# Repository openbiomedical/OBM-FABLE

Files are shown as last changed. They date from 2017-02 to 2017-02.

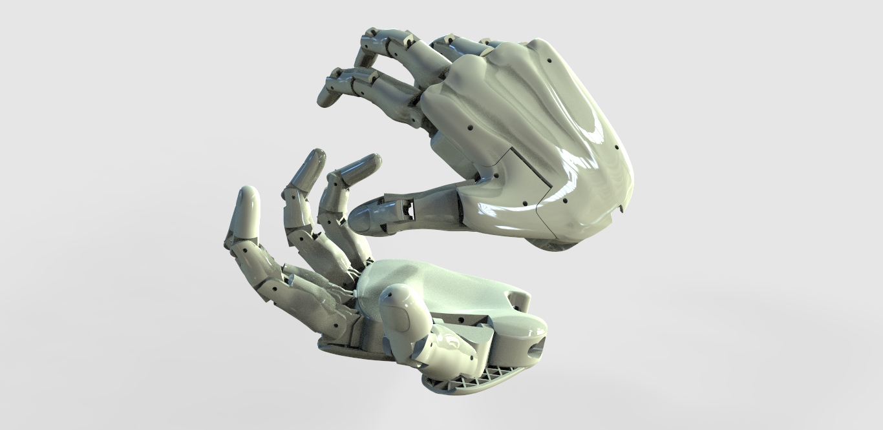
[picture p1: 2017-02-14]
3D Model/FABLE _V0.1 _April _2015/pics/2 posizione 2 bis.jpg

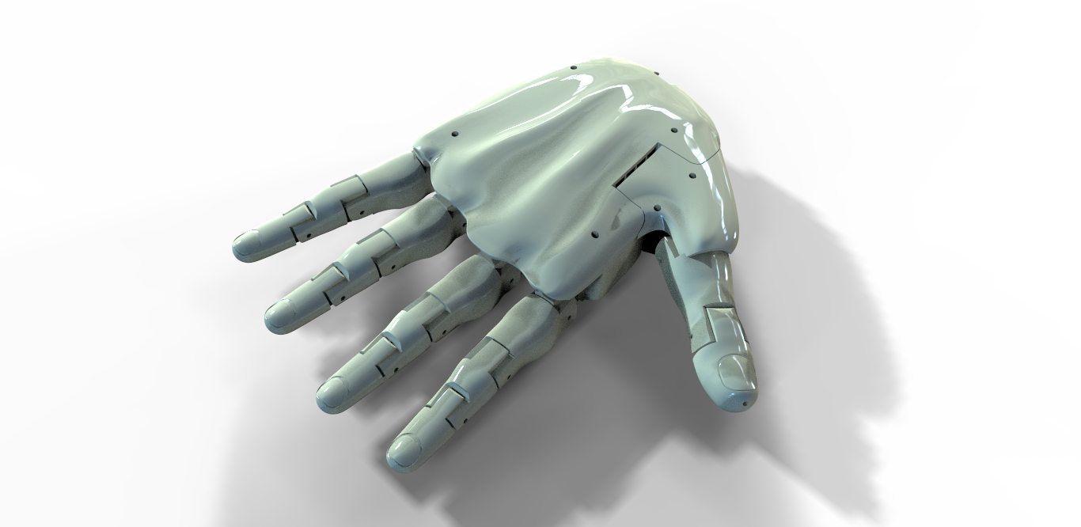
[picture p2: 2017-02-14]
3D Model/FABLE _V0.1 _April _2015/pics/1 luce 2.jpg

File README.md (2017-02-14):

# OBM-FABLE
FABLE is an electromechanical hand. Through the acquisition of signals generated by the muscles myoelectric contraction next to the elbow, it determines precise finger movements. Electronics is the hub of the system and it is compact, lowcost, completely reengineered to provide a project everywhere reproducible and technologically advanced. This hand is not a prosthesis, it is intended as a development kit. This work is licensed under the Creative Commons Attribution-NonCommercial-ShareAlike 4.0 International License. To view a copy of this license, visit https://creativecommons.org/licenses/by-nc-sa/4.0/legalcode

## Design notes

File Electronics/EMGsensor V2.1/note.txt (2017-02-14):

from Vin to electrodes only shield cable ( shield = pin2)

reference electrode = GND

supply from 5vdc to 12vdc (stab.)

R14 = gain

Shift = output with offset (Vcc/2)

no_shift = Output without offset (Vcc/2)

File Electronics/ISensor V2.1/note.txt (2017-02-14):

Resistor smd 2512 package

PS1,..,PS6 = to arduino [ PWM = pin3 ; Analog Input = pin1 ]

S1,...,S6 = From servo  [ PWM = Pin3 ; VCC = Pin2 ; GND = pin1 to resistor ]

VCC = 6v dc Max from step-down

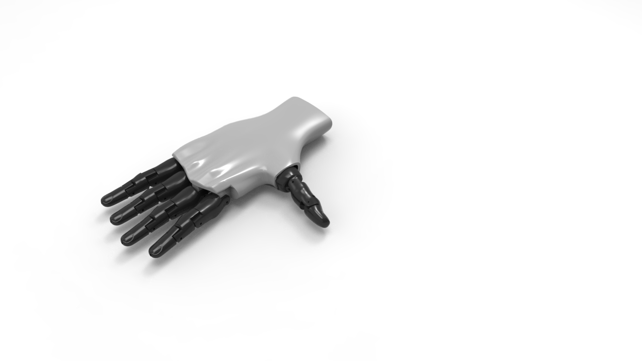
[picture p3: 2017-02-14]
3D Model/FABLE V0.2 August 2015/pics/untitled.222.jpg

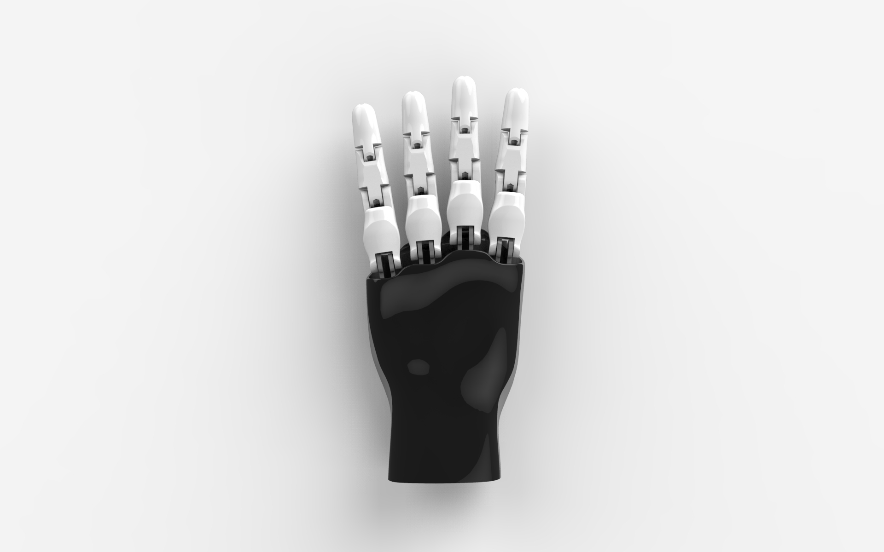
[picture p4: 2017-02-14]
3D Model/FABLE V0.2 August 2015/pics/untitled.328.jpg

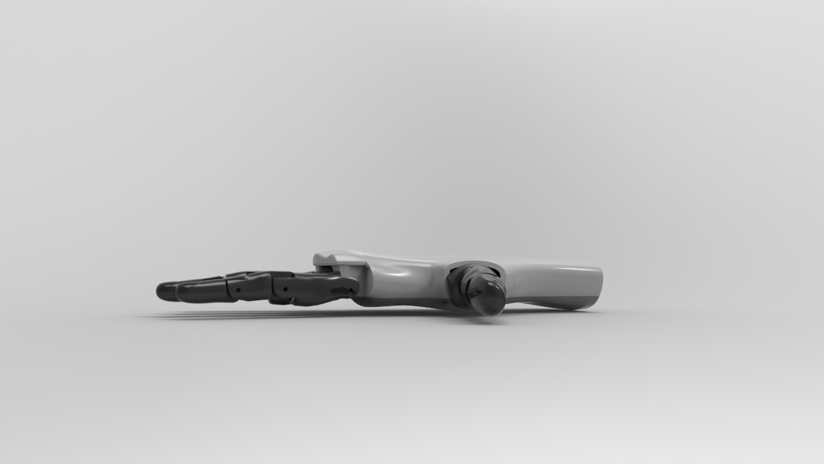
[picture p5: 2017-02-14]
3D Model/FABLE V0.2 August 2015/pics/untitled.223.jpg

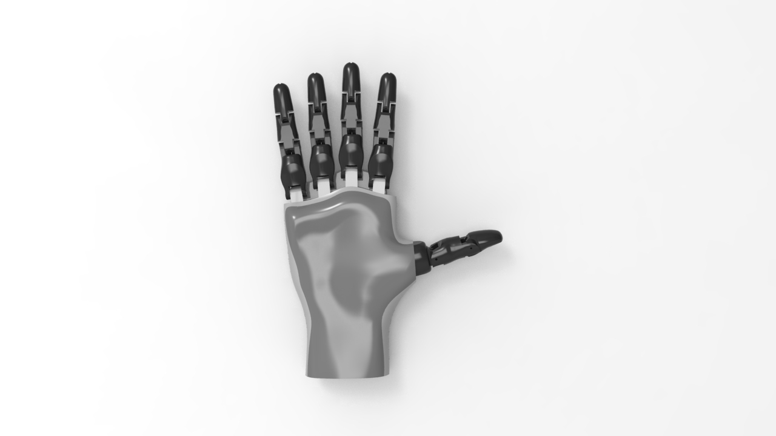
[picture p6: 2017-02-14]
3D Model/FABLE V0.2 August 2015/pics/untitled.217.jpg

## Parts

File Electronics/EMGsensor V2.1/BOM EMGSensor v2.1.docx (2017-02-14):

Componenti EMGSensor v2.1

Resistors | Pz. | Codice | Link
3,9k 1% | 2 | | http://www.mouser.it/ProductDetail/KOA-Speer/MF1-4DCT52R3901F/?qs=sGAEpiMZZMsPqMdJzcrNwk4M%252bI85OEMF%252b8B6SFnC314%3d
2,7k 1% | 1 | | http://www.mouser.it/ProductDetail/KOA-Speer/MF1-4DCT52R2701F/?qs=sGAEpiMZZMsPqMdJzcrNwk4M%252bI85OEMFHm1ljwxmljk%3d
330k 1% | 4 | | http://www.mouser.it/ProductDetail/KOA-Speer/MF1-4DCT52R3303F/?qs=sGAEpiMZZMsPqMdJzcrNwk4M%252bI85OEMF4k6263vO8XI%3d
150k 1% | 2 | | http://www.mouser.it/ProductDetail/KOA-Speer/MF1-4CCT52R1503F/?qs=sGAEpiMZZMsPqMdJzcrNwk4M%252bI85OEMFH8UroyRjCLw%3d
10k 1% | 3 | | http://www.mouser.it/ProductDetail/KOA-Speer/MF1-4DCT52A1002F/?qs=sGAEpiMZZMsPqMdJzcrNwuecx6lsmnwYT8hyjLelWtY%3d
22k 1% | 3 | | http://www.mouser.it/ProductDetail/KOA-Speer/MF1-4CCT52R2202F/?qs=sGAEpiMZZMsPqMdJzcrNwk4M%252bI85OEMFeFz33mmpMTA%3d
100k trim | 1 | | http://www.mouser.it/ProductDetail/BI-Technologies-TT-Electronics/25PR100KLF/?qs=sGAEpiMZZMvygUB3GLcD7jZSyzxDqivkrwCWYpHkBsI%3d

Capacitors | Pz | Codice | Link
1nF 5% | 2 | | http://www.mouser.it/ProductDetail/Kemet/R82EC1100DQ50J/?qs=sGAEpiMZZMv1cc3ydrPrF512ADDNLQZJj36DMWUqyRU%3d
10nF 5% | 1 | | http://www.mouser.it/ProductDetail/WIMA/FKP2-01-63-5/?qs=sGAEpiMZZMv1cc3ydrPrF9SBthQCDPcr2mIDPeCmXKk%3d
47 uF 16v | 1 | | http://www.mouser.it/ProductDetail/Kemet/ESH476M016AC3AA/?qs=sGAEpiMZZMvwFf0viD3Y3Z8dpVAM7bD5NxuBo6CNc2U%3d
100nF | 3 | | http://www.mouser.it/ProductDetail/Xicon/140-50U5-104M-RC/?qs=sGAEpiMZZMt1mVBmZSXTPPQUnq7ol7tGZljKIuTg6iI%3d
33nF | 4 | | http://www.mouser.it/ProductDetail/WIMA/MKS20-033-63-10/?qs=sGAEpiMZZMv1cc3ydrPrF9fbJRxYhp3ITJ3n2D%252bCNEc%3d
3,9nF | 2 | | http://www.mouser.it/ProductDetail/Kemet/MMK5392J63J01L165TR18/?qs=sGAEpiMZZMv1cc3ydrPrF17gIuUB4mH1M9xivW0kULQ%3d

Ic, diode | Pz. | Codice | Link
schotty | 1 | | http://www.mouser.it/ProductDetail/STMicroelectronics/STPS2150/?qs=sGAEpiMZZMtQ8nqTKtFS%2fM2amOy8Xbj2uDkMBx8%252beH4%3d
Ad623br | 1 | | http://www.mouser.it/ProductDetail/Analog-Devices/AD623BNZ/?qs=sGAEpiMZZMv9Q1JI0Mo%2fteUpiLyE8W1%2f
Opa4342 | 1 | | http://www.mouser.it/ProductDetail/Texas-Instruments/OPA4342PA/?qs=sGAEpiMZZMtCHixnSjNA6Mrdwin7F8A2Bb6eRblE8YI%3d

vari | Pz. | Codice | Link
Socket 8pin | 1 | | http://it.rs-online.com/web/p/zoccoli-dil/6742479/
Socket 14pin | 1 | | http://it.rs-online.com/web/p/zoccoli-dil/6742476/
Porta batterie | 1 | | http://www.mouser.it/ProductDetail/Keystone-Electronics/1049P/?qs=sGAEpiMZZMt13fpse6CWDXAPAJ%2f5HJNvHuGSwYCxUME7UjRmTs2TpQ%3d%3d

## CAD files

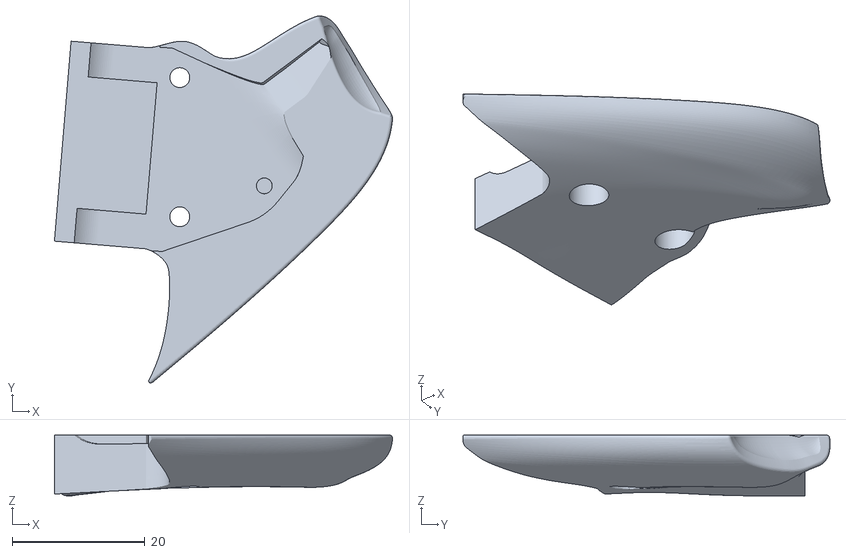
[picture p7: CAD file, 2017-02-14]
3D Model/FABLE _V0.1 _April _2015/stl_v0.1/Copertura snodo/copertura snodo008.stl
51.0 x 55.4 x 9.19

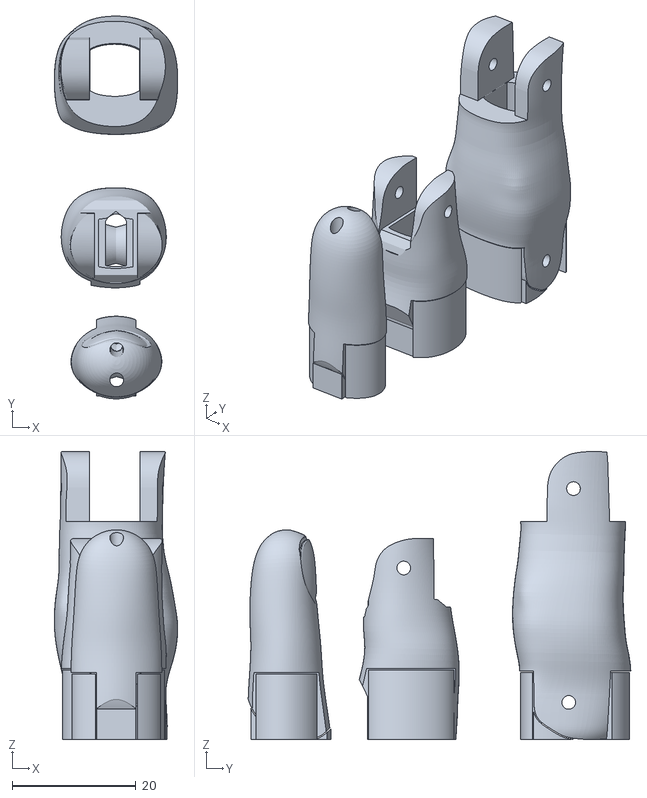
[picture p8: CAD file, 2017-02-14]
3D Model/FABLE _V0.1 _April _2015/stl_v0.1/Dita/dita 002 Supporti.stl
20.0 x 61.9 x 46.6

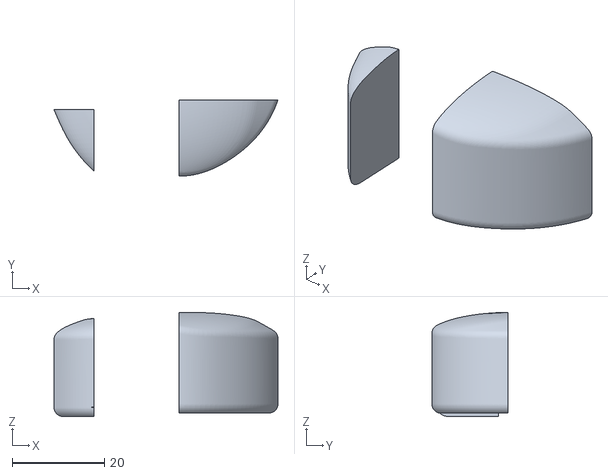
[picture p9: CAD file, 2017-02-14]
3D Model/FABLE _V0.1 _April _2015/stl_v0.1/Pezzi Palmo/pezzi_palmo001.stl
48.5 x 16.5 x 22.6

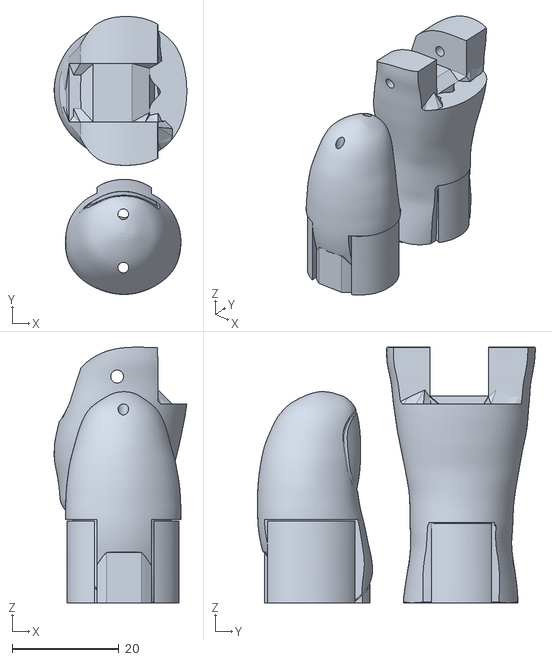
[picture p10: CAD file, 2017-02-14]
3D Model/FABLE _V0.1 _April _2015/stl_v0.1/Pollice/pollice001 supporti.stl
24.9 x 52.2 x 48.0

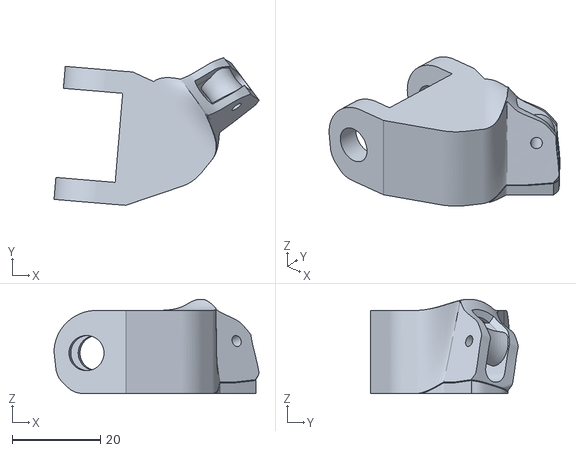
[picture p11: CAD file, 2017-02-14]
3D Model/FABLE _V0.1 _April _2015/stl_v0.1/Snodo/snodo004 supporto.stl
46.5 x 33.5 x 21.4

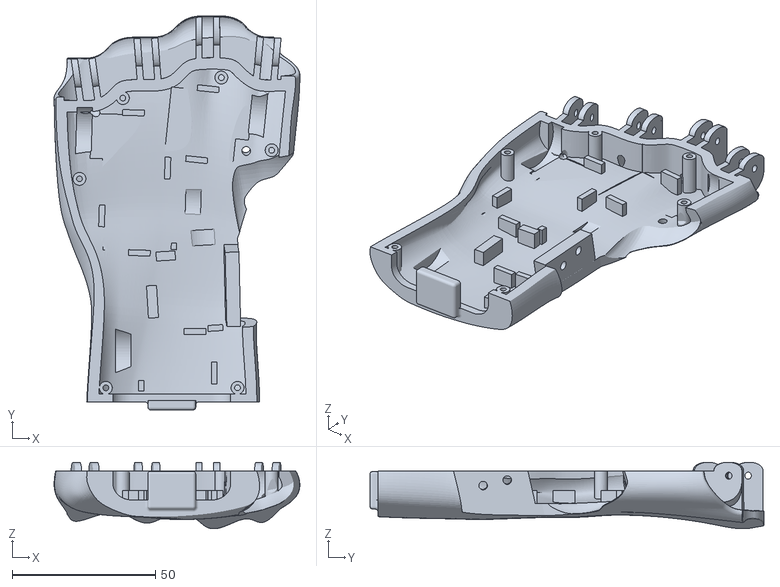
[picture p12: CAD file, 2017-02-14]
3D Model/FABLE V0.2 August 2015/STL v0.2 agosto 2015/dorso.stl
85.7 x 137.4 x 23.2

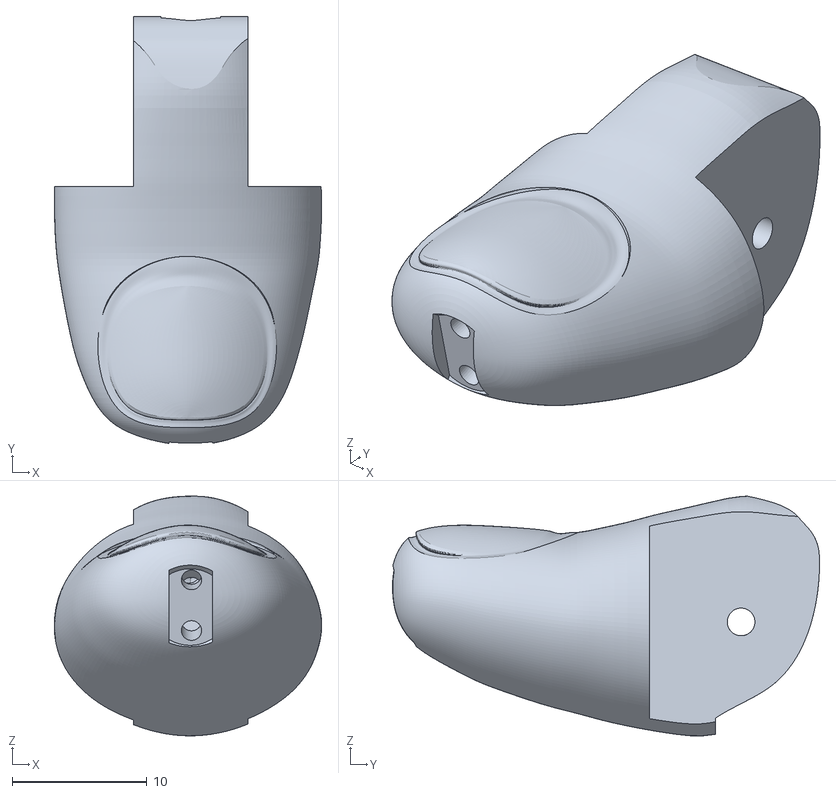
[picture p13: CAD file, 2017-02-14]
3D Model/FABLE V0.2 August 2015/STL v0.2 agosto 2015/stl_dita/pollice2.stl
19.9 x 31.7 x 17.8

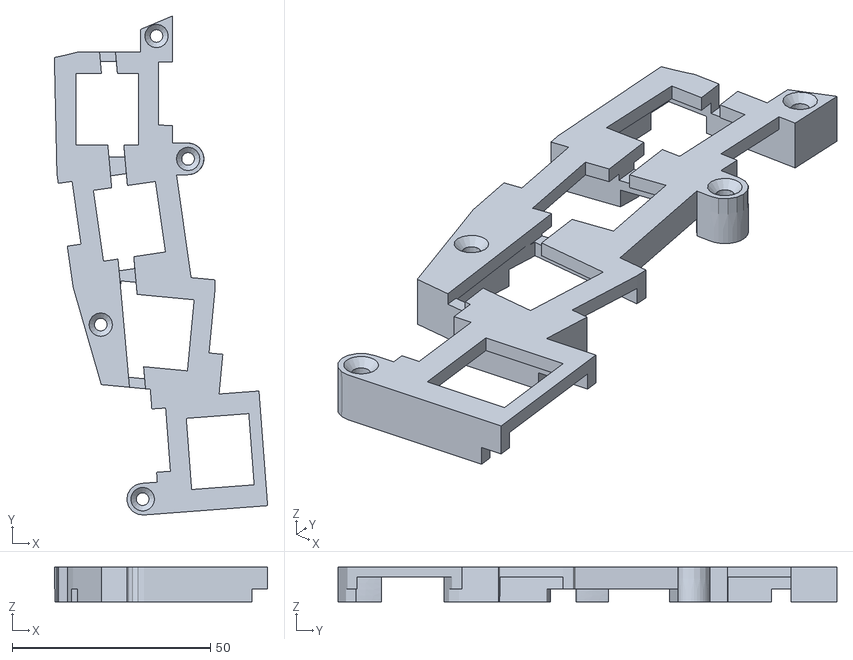
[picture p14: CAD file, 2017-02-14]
3D Model/fable v0.3 January 2016/FABLE V0.3 STL january 2016/coperchio servo.stl
53.8 x 125.8 x 8.80

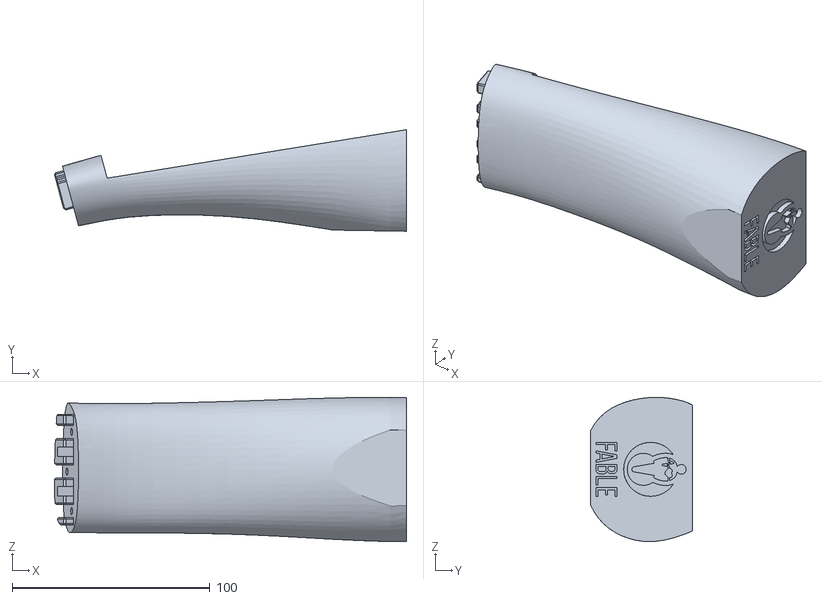
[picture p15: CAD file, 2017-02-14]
3D Model/FABLE V0.4 September 2016/STL V0.4/support front arm stl/support front.stl
178.0 x 51.4 x 72.9

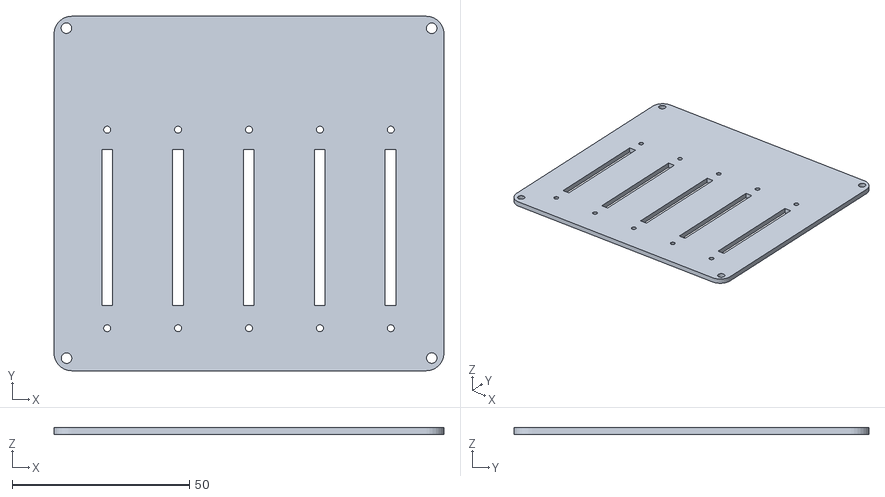
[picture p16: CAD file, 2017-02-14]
3D Model/FABLE V0.4 September 2016/STL V0.4/support pot stl/plate pot.stl
110.0 x 100.0 x 2.00

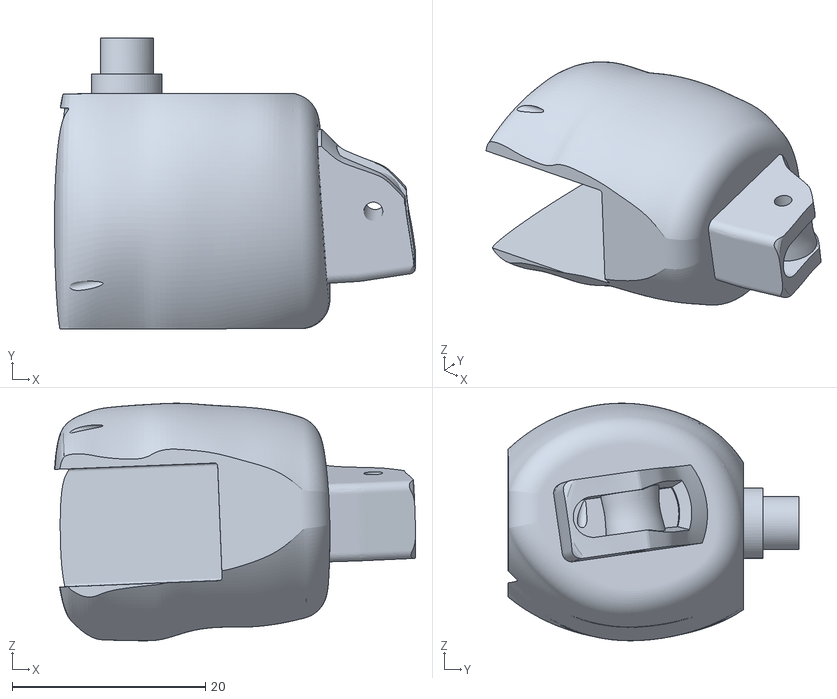
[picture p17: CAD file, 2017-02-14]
3D Model/FABLE V0.2 August 2015/STL v0.2 agosto 2015/snodo pollice.stl
37.4 x 30.2 x 24.6

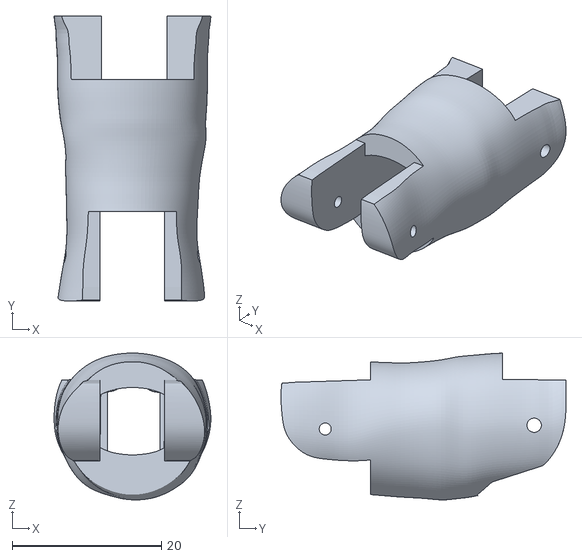
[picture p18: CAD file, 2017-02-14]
3D Model/FABLE V0.2 August 2015/STL v0.2 agosto 2015/stl_dita/pollice1.stl
21.0 x 38.2 x 19.7

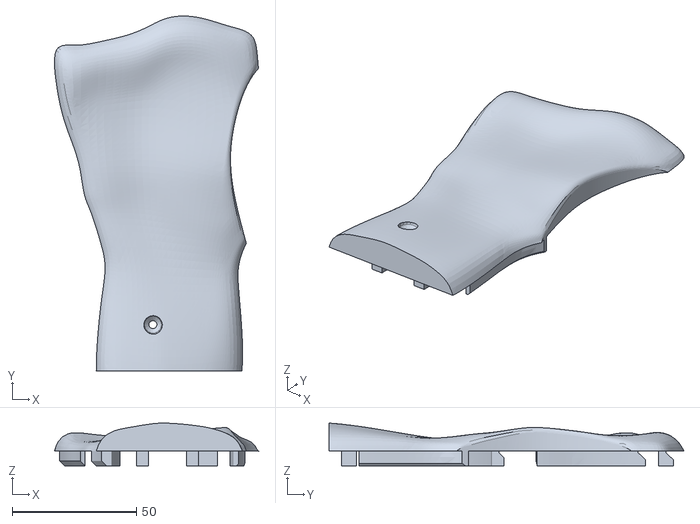
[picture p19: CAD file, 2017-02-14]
3D Model/fable v0.3 January 2016/FABLE V0.3 STL january 2016/palmo fable.stl
82.1 x 142.9 x 17.3

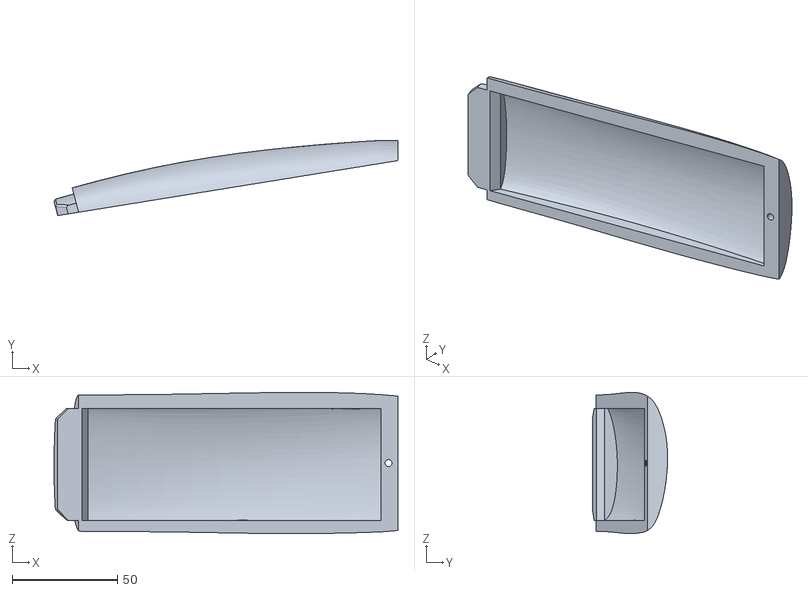
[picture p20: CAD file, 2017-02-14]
3D Model/FABLE V0.4 September 2016/STL V0.4/support front arm stl/support back.stl
163.1 x 35.7 x 66.9

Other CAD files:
3D Model/FABLE V0.4 September 2016/STL V0.4/support pot stl/structure.stl
3D Model/FABLE V0.2 August 2015/STL v0.2 agosto 2015/palmo.stl
3D Model/FABLE V0.2 August 2015/STL v0.2 agosto 2015/stl_dita/dito3.stl
3D Model/FABLE V0.4 September 2016/STL V0.4/support pot stl/plate arduino nano.stl
3D Model/FABLE V0.2 August 2015/STL v0.2 agosto 2015/blocco1.stl
3D Model/FABLE V0.2 August 2015/STL v0.2 agosto 2015/blocco2.stl
3D Model/FABLE V0.2 August 2015/STL v0.2 agosto 2015/stl_dita/dito1.stl
3D Model/FABLE V0.2 August 2015/STL v0.2 agosto 2015/stl_dita/dito2.stl
3D Model/FABLE V0.2 August 2015/STL v0.2 agosto 2015/stl_dita/falange orizzontale supporto.stl
3D Model/FABLE V0.4 September 2016/3dm v0.4/hand/finger.3dm
3D Model/FABLE V0.4 September 2016/3dm v0.4/hand/hand back.3dm
3D Model/FABLE V0.4 September 2016/3dm v0.4/hand/hand palm.3dm
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

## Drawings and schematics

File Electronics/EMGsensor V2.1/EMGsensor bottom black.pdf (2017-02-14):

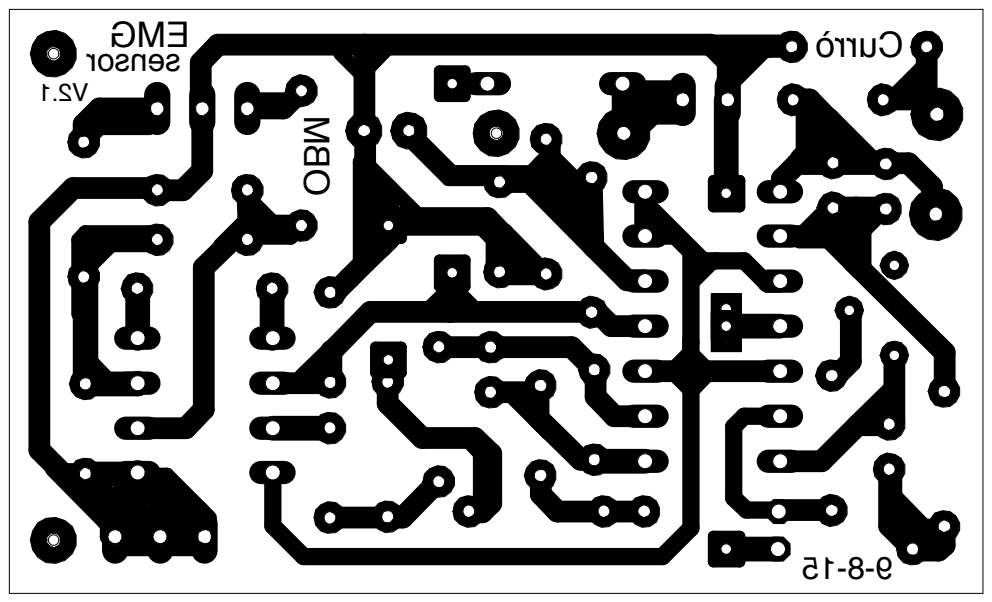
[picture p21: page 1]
EMG sensorV2.1; OBM; Currò

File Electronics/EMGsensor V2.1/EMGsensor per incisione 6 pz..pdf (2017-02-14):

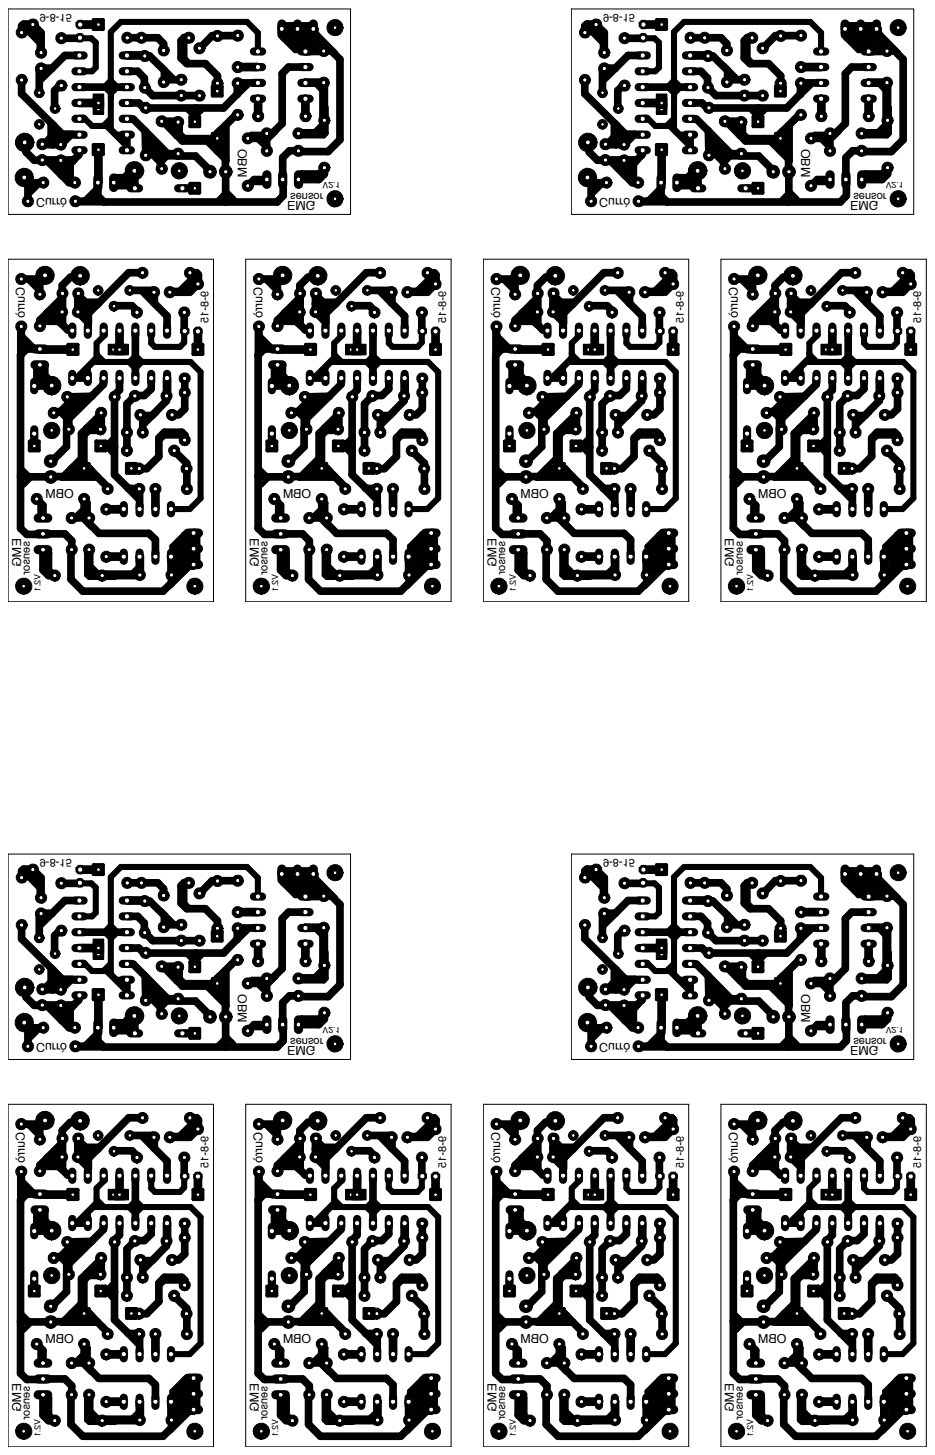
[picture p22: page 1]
EMG sensor; Currò; EMG; sensorV2.1; OBM

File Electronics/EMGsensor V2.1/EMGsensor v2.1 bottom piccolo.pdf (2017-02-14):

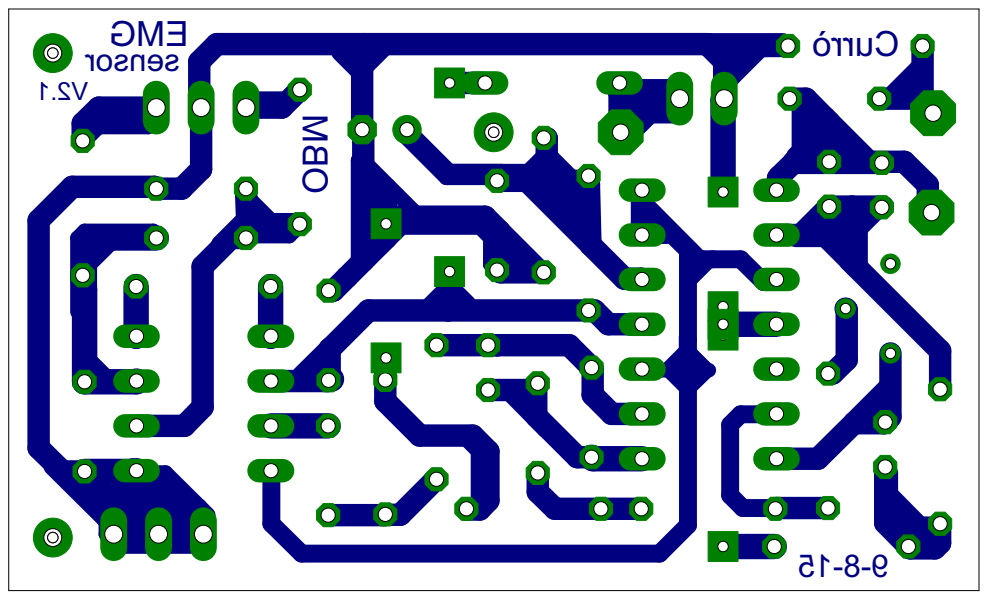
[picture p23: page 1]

GME r osnes 1. 2V OBM òrr uC 51- 8- 9

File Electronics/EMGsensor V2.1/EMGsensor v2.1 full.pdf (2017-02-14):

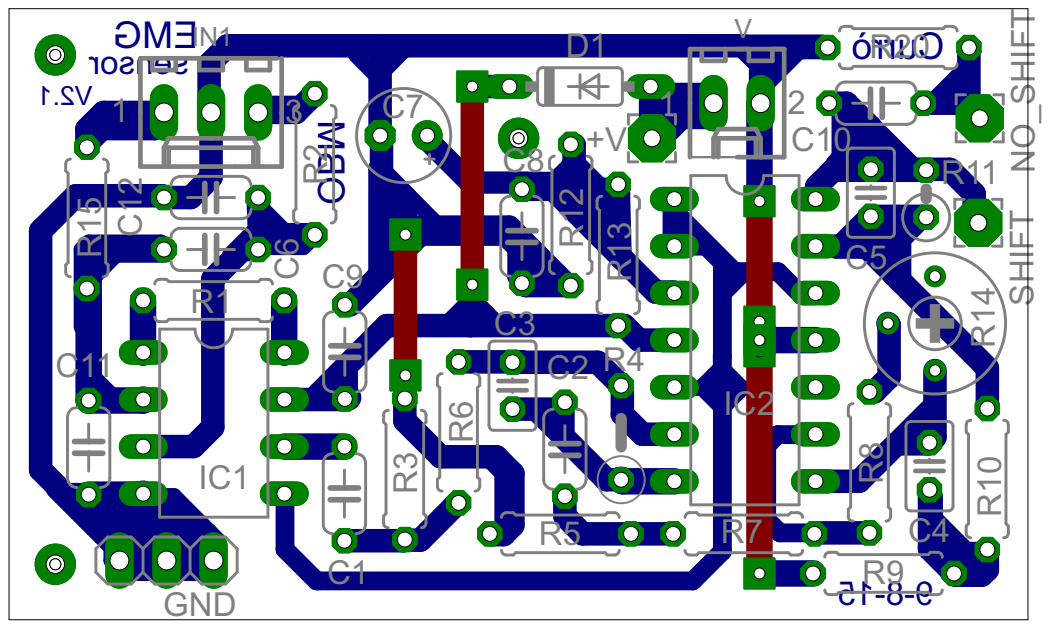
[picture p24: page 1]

GME r osnes 1. 2V OBM òrr uC 51- 8- 9 1 1 2 3 C1 C2 C3 C4 C5 C7 C8 C9 D1 IC1 IC2 NO_SHIFT SHIFT R1 R10 R12 R13 R14 R3 R4 R5 R6 R7 R8 R9 +V V GND R20 C10 C6 C11 C12R2 R15 IN1 R11

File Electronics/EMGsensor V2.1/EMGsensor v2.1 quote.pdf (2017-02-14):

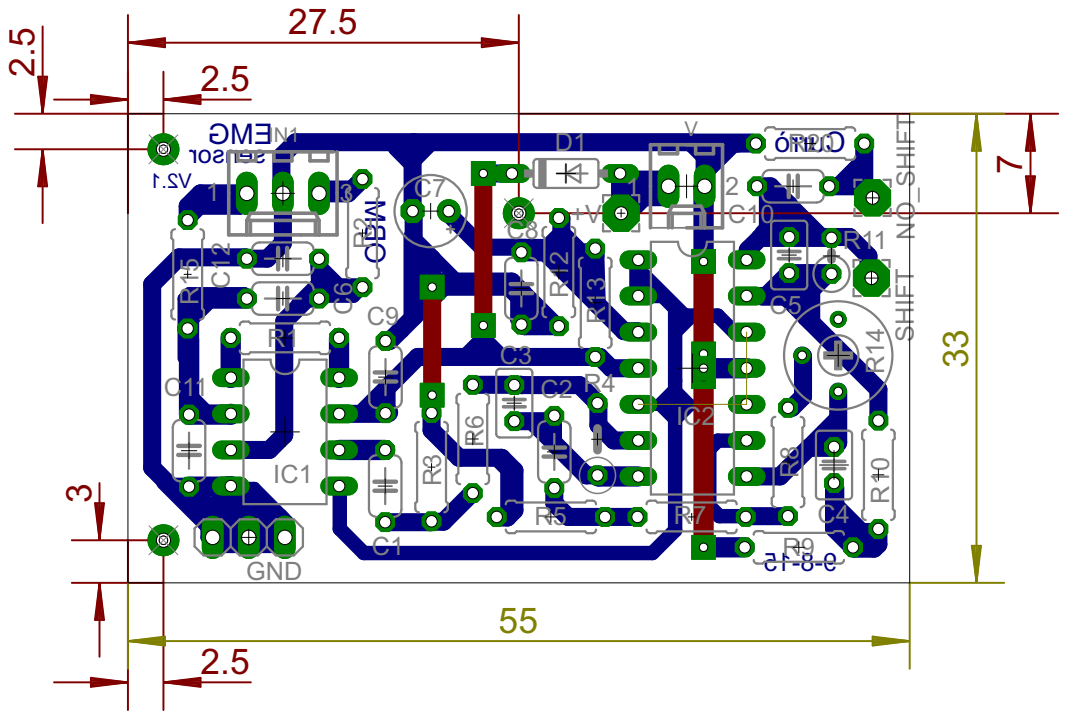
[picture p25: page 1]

GME r osnes 1. 2V OBM òrr uC 51- 8- 9 2.5 2.5 2.5 3 27.5 7 1 1 2 3 C1 C2 C3 C4 C5 C7 C8 C9 D1 IC1 IC2 NO_SHIFT SHIFT R1 R10 R12 R13 R14 R3 R4 R5 R6 R7 R8 R9 +V V GND R20 C10 C6 C11 C12R2 R15 IN1 R11 55 33

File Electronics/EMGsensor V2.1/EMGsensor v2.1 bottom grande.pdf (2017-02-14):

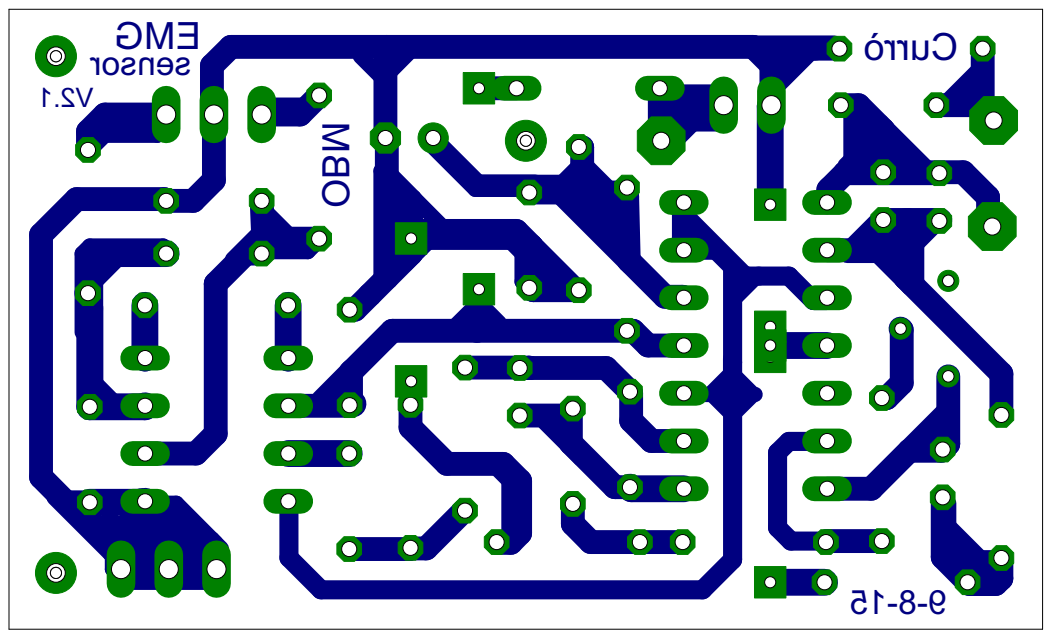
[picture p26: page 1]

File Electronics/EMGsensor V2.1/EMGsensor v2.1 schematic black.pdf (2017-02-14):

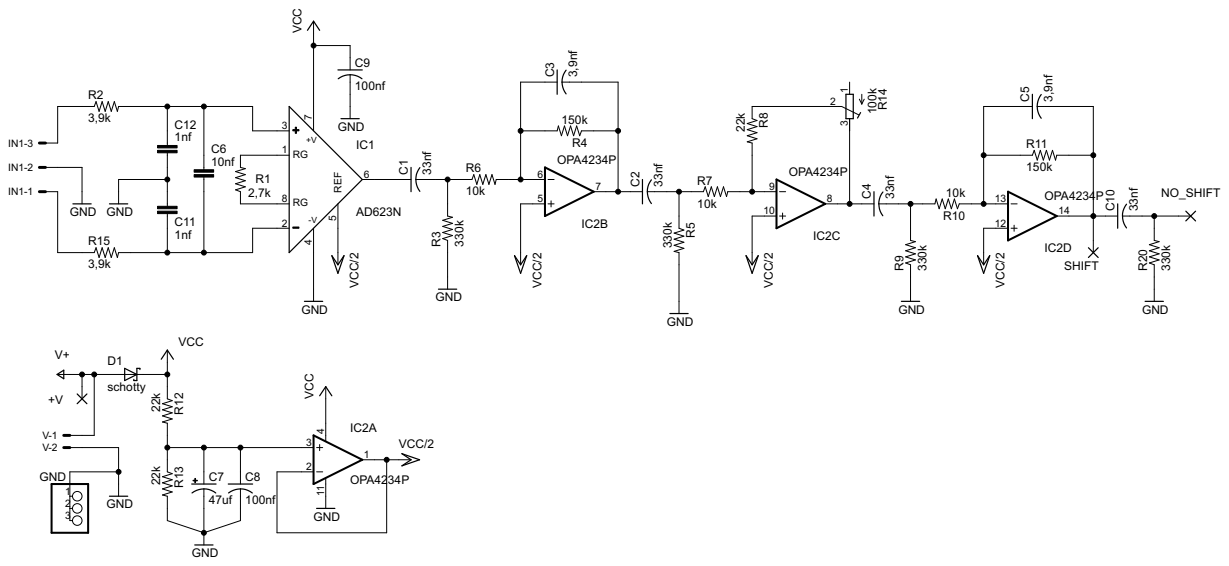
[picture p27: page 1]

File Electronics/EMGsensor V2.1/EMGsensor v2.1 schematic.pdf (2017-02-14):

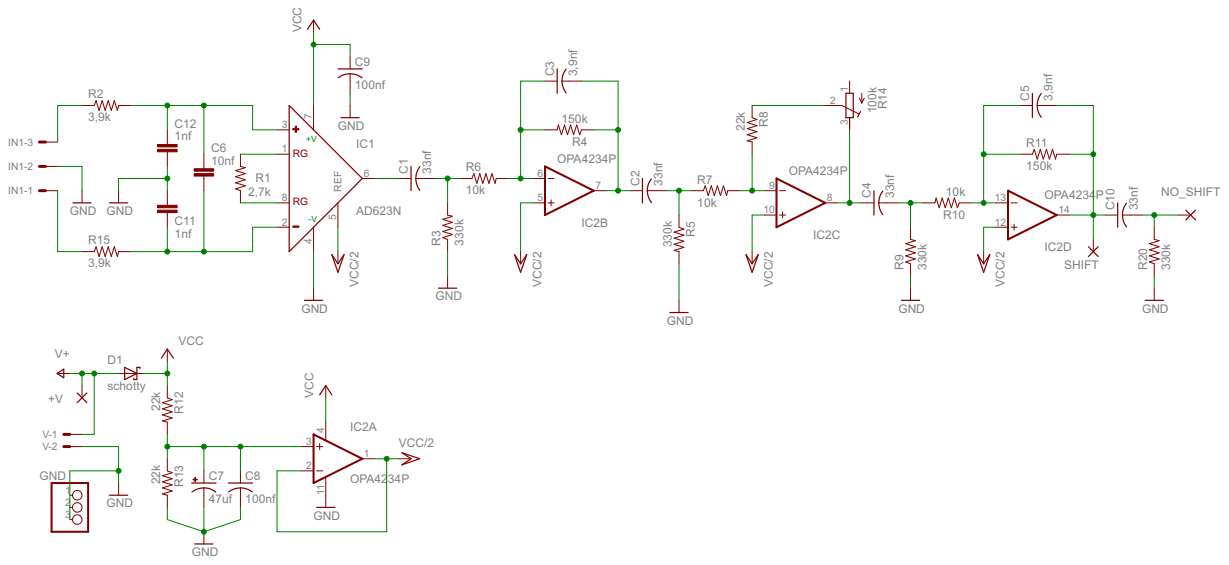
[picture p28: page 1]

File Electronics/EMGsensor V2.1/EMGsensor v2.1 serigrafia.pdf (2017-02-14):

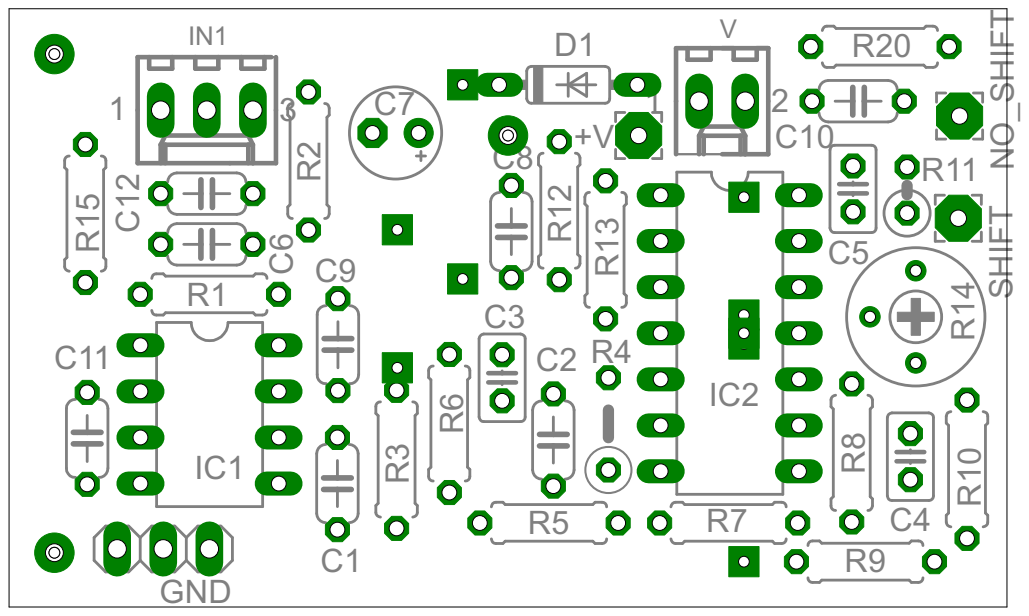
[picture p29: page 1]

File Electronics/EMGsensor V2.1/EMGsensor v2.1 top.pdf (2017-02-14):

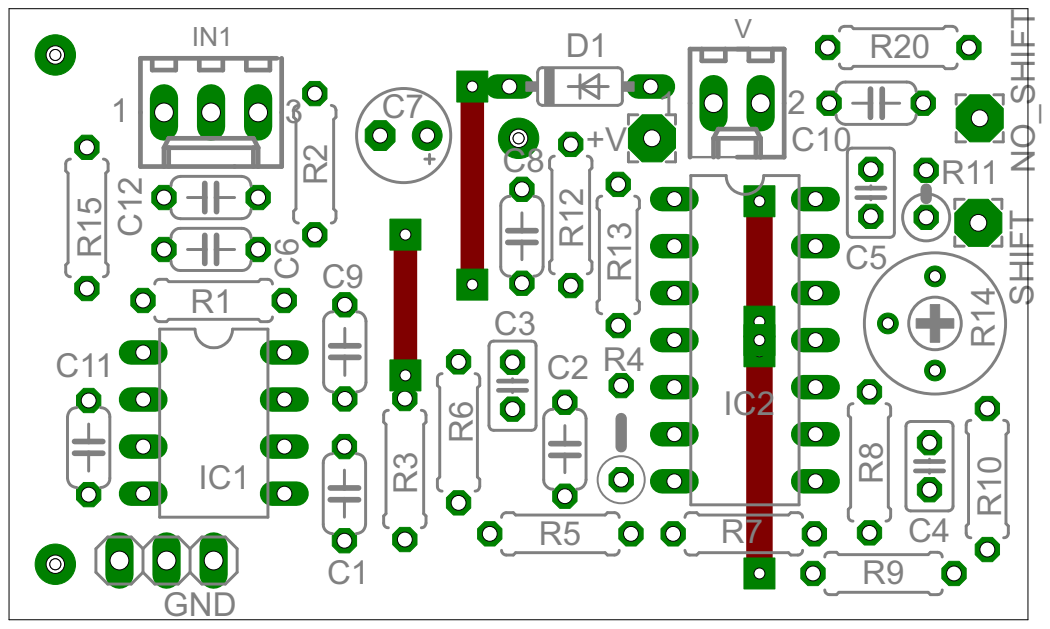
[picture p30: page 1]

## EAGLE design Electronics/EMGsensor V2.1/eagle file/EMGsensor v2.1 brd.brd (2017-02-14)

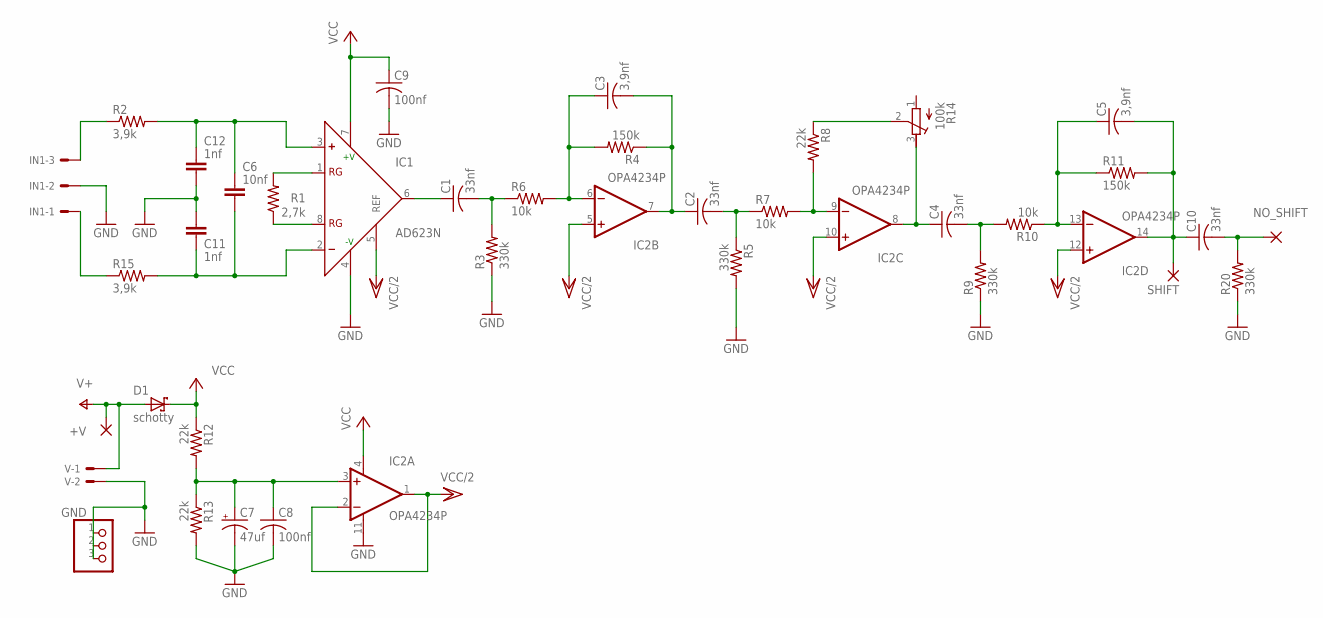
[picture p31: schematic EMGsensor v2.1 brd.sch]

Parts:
+V: 2,54/0,9
C1, C2, C10: 33nf; C050-024X044
C3, C5: 3,9nf; C025-025X050
C4: 33nf; C025-025X050
C6: 10nf; C050-024X044
C7: 47uf; E2,5-5
C8, C9: 100nf; C050-024X044
C11, C12: 1nf; C050-024X044
D1: schotty; DO35-7
GND: PINHD-1X3; 1X03
IC1: AD623N; DIL08
IC2: OPA4234P; DIL14
IN1: 22-27-2031-03; 6410-03
NO_SHIFT: 2,54/0,9
R1: 2,7k; 0207/7
R2, R15: 3,9k; 0207/7
R3, R5, R9, R20: 330k; 0207/7
R4: 150k; 0207/5V
R6, R7, R10: 10k; 0207/7
R8, R12, R13: 22k; 0207/7
R11: 150k; 0207/2V
R14: 100k; RTRIM3339P
SHIFT: 2,54/0,9
V: 22-27-2021-02; 6410-02

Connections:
unnamed: C1.1, IC1.6 (OUT)
unnamed: C1.2, R3.2, R6.1
unnamed: C3.1, IC2.6 (-IN), R4.2, R6.2
unnamed: C2.1, C3.2, IC2.7 (OUT), R4.1
unnamed: C2.2, R5.1, R7.1
unnamed: IC2.9 (-IN), R7.2, R8.2
unnamed: C4.1, IC2.8 (OUT), R14.3 (E)
unnamed: C4.2, R9.2, R10.2
unnamed: C5.1, IC2.13 (-IN), R10.1, R11.1
unnamed: C5.2, C10.1, IC2.14 (OUT), R11.2, SHIFT.1
unnamed: R8.1, R14.2 (S)
unnamed: IC1.1 (RG), R1.2
unnamed: C6.1, C12.1, IC1.3 (+), R2.2
unnamed: C6.2, C11.2, IC1.2 (-), R15.2
unnamed: IN1.3, R2.1
unnamed: C10.2, NO_SHIFT.1, R20.2
unnamed: IN1.1, R15.1
unnamed: IC1.5 (REF), IC2.1 (OUT), IC2.2 (-IN)
unnamed: C9.1, D1.C, IC1.7 (+V), IC2.4 (V+), R12.1
unnamed: C7.+, C8.1, IC2.3 (+IN), R12.2, R13.1
unnamed: +V.1, D1.A, V.1
unnamed: IC1.8 (RG), R1.1
unnamed: C7.-, C8.2, C9.2, C11.1, C12.2, GND.1, GND.2, GND.3, IC1.4 (-V), IC2.11 (V-), IN1.2, R3.1, R5.2, R9.1, R13.2, R20.1, V.2
VCC/2: IC2.5 (+IN), IC2.10 (+IN), IC2.12 (+IN)

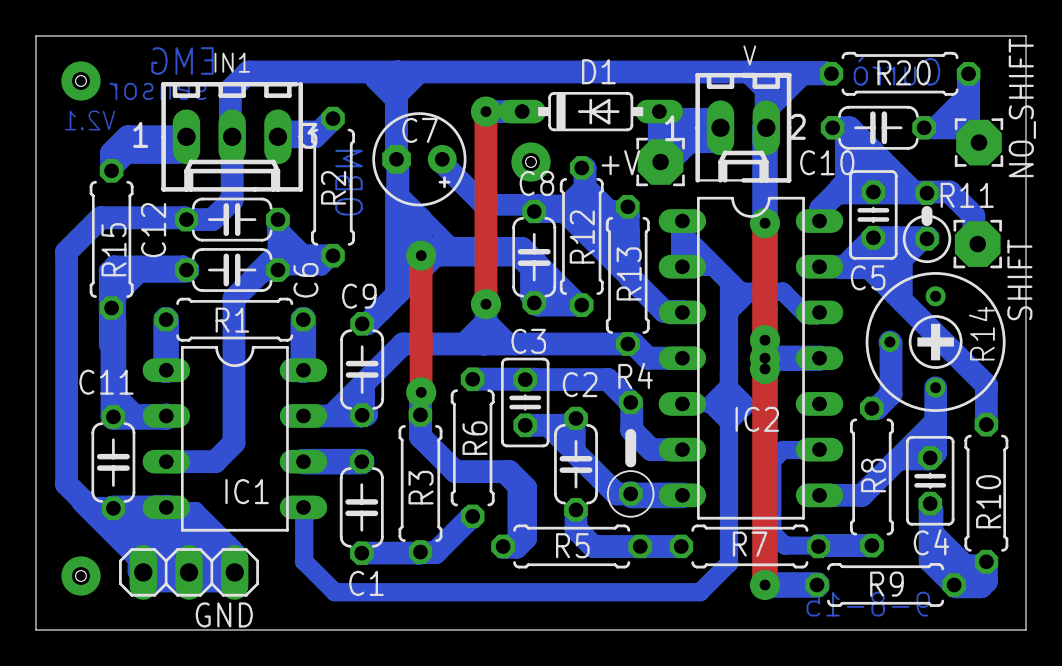
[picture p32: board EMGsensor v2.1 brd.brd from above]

Board: 2 copper layers, 55.0 x 33.0 mm, 37 parts (0 on the bottom side), 24 nets.

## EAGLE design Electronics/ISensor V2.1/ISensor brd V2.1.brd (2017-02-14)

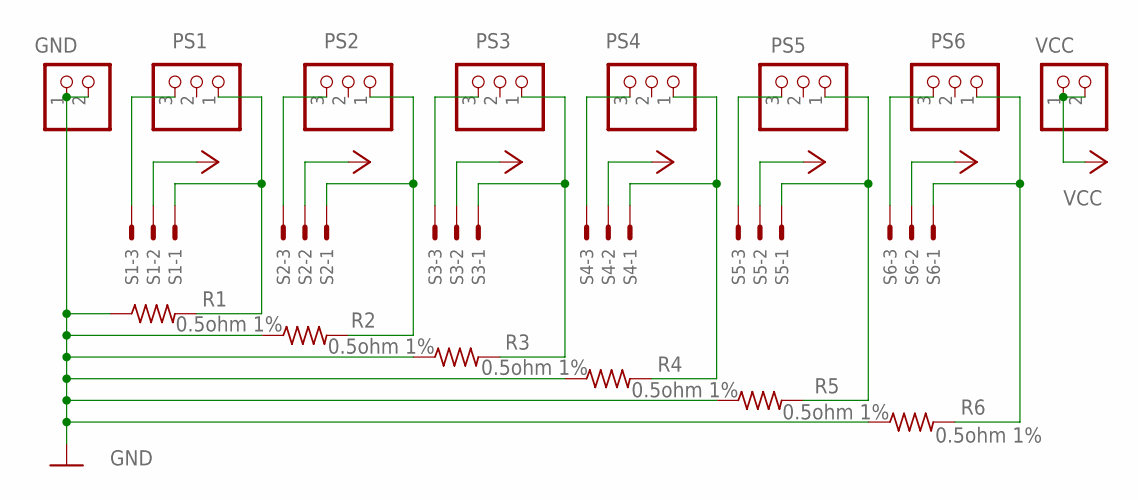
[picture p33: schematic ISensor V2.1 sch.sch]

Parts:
GND: PINHD-1X2; 1X02
PS1, PS2, PS3, PS4, PS5, PS6: PINHD-1X3; 1X03
R1, R2, R3, R4, R5, R6: 0.5ohm 1%; R2512
S1, S2, S3, S4, S5, S6: 22-27-2031-03; 6410-03
VCC: PINHD-1X2; 1X02

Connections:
unnamed: PS1.3, S1.3
unnamed: PS1.1, R1.2, S1.1
unnamed: PS2.1, R2.2, S2.1
unnamed: PS3.3, S3.3
unnamed: PS3.1, R3.2, S3.1
unnamed: PS4.3, S4.3
unnamed: PS4.1, R4.2, S4.1
unnamed: PS5.3, S5.3
unnamed: PS5.1, R5.2, S5.1
unnamed: PS6.3, S6.3
unnamed: PS6.1, R6.2, S6.1
unnamed: GND.1, GND.2, R1.1, R2.1, R3.1, R4.1, R5.1, R6.1
PS2: PS2.3, S2.3
VCC: S1.2, S2.2, S3.2, S4.2, S5.2, S6.2, VCC.1, VCC.2

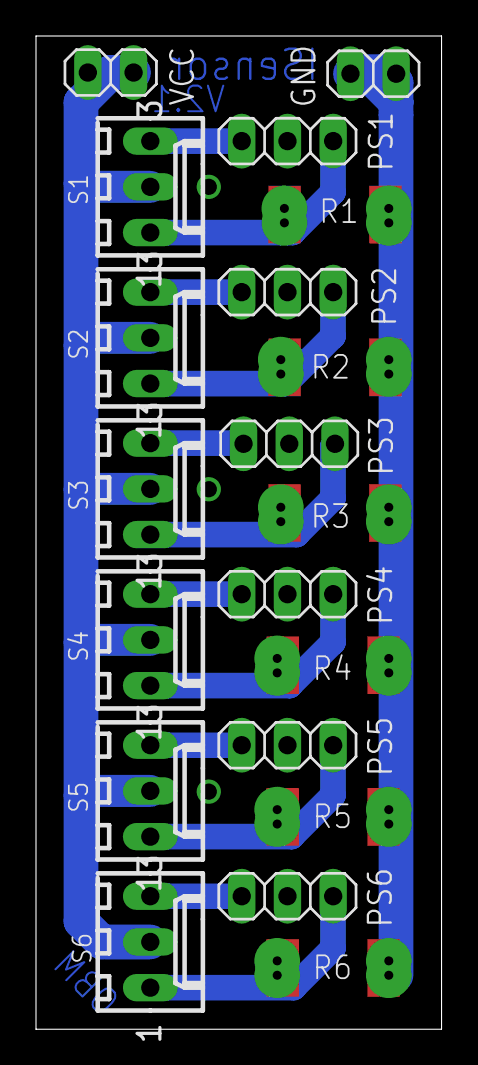
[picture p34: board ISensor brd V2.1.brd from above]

Board: 2 copper layers, 22.5 x 55.2 mm, 20 parts (0 on the bottom side), 14 nets.

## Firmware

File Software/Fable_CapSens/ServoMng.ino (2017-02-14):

int GetServoPos(int ServoIndex){
  return ArmoMov.angolo[ServoIndex];
  }
void SetServoPos(int ServoIndex, int Pos){
  ArmoMov.Pos[ServoIndex]=Pos;  
  }
  
void SetServoAngleMin (int ServoIndex,int AngleMin){
  FABLE_InfoParameter.OpenAngleTarget[ServoIndex]=AngleMin;
  }

void SetServoAngleMax (int ServoIndex,int AngleMax){
  FABLE_InfoParameter.CloseAngleTarget[ServoIndex]=AngleMax;
  }
void SetEnableFinger(int FingerCode){
  }
int GetEnablefinger(){
   int EnableCount=0;
   for (int i =0;i<NumServo;i++)
    EnableCount+=FABLE_InfoParameter.FingerEnabled[i];
  return EnableCount;
  }  
int GetServoAngleMin (int ServoIndex){
  return FABLE_InfoParameter.OpenAngleTarget[ServoIndex];
  }

 int GetServoAngleMax (int ServoIndex){
  return FABLE_InfoParameter.CloseAngleTarget[ServoIndex];
  }

int GetServoSpeed(){
  return FABLE_InfoParameter.Speed;
   }

void SetServoSpeed(int Speed){
  FABLE_InfoParameter.Speed=Speed;
  }



void MoveServo(int ServoIndex){
  
  int Speed=GetServoSpeed();
  int anglemin=GetServoAngleMin(ServoIndex);
  int anglemax=GetServoAngleMax(ServoIndex);
  float Stepmin=(anglemax-anglemin);
  float AngleStep=(Stepmin*Speed)/1048 ;
  int CurrPos=GetServoPos(ServoIndex);
  
 // Serial.println(Stepmin);
 // Serial.println(anglemin);
 // Serial.println(anglemax);
 // Serial.println(AngleStep);
  if (ArmoMov.Pos[ServoIndex]<CurrPos){
      AngleStep=-AngleStep;
      while(ArmoMov.grado[ServoIndex]>ArmoMov.Pos[ServoIndex])
      {ServoMovement(ServoIndex,AngleStep);
      Serial.println(ArmoMov.grado[ServoIndex]);}
      
      }
   else{
    while(ArmoMov.grado[ServoIndex]<ArmoMov.Pos[ServoIndex])
    {ServoMovement(ServoIndex,AngleStep);
    Serial.println(ArmoMov.grado[ServoIndex]);}
    
    }
  
  
  }
  
void MoveFinger(int index,int Pos){
  SetServoPos(index,Pos);
  MoveServo(index);
  
  }

void OpenHand(){
  for (int i=0;i<NumServo;i++){
    MoveFinger(i,FABLE_InfoParameter.OpenAngleTarget[i]);
   delay(FABLE_InfoParameter.FingerDelay);
  }
  
  
  }

void CloseHand(){
  for (int i=0;i<NumServo;i++){
    MoveFinger(i,FABLE_InfoParameter.CloseAngleTarget[i]);
    //FableCom.write("MoveFinger",i);
   delay(FABLE_InfoParameter.FingerDelay);
  }
  
  }

void ServoMovement(int ServoIndex,float AngleStep){
    //float stepnum=(Servoanglemax-Servoanglemin)/pos ;
  
  int anglemin=5;//GetServoAngleMin(ServoIndex);
  int anglemax=160;//GetServoAngleMax(ServoIndex);
  
 float sen = sin(PI*ArmoMov.angolo[ServoIndex]/180);
 // coseno=cos( (angolo[Servoindex]/rad2grad) );
 ArmoMov.grado[ServoIndex] =  (sen*((anglemax-anglemin)/2))+((anglemax+anglemin)/2) ;
 
  FABLE_Servo[ServoIndex].write(ArmoMov.grado[ServoIndex]);
  
 ArmoMov.angolo[ServoIndex]=ArmoMov.angolo[ServoIndex]+AngleStep;
 
 }
 
void SetDefaultParameter(){

  FABLE_DefaultParameter.LevelShift =512;
  FABLE_DefaultParameter.OverRatio=2;
  FABLE_DefaultParameter.CalibrationTime=4000;
  FABLE_DefaultParameter.tau=0.095;
  FABLE_DefaultParameter.csens_thr=0.3;
  FABLE_DefaultParameter.OvercurrentAngle=5;
  FABLE_DefaultParameter.Speed=50;
  for (int i=0;i<5;i++)
    FABLE_DefaultParameter.FingerEnabled[i]=1;
  
  FABLE_DefaultParameter.CloseAngleTarget[0]=150;
  FABLE_DefaultParameter.CloseAngleTarget[1]=150;
  FABLE_DefaultParameter.CloseAngleTarget[2]=150;
  FABLE_DefaultParameter.CloseAngleTarget[3]=150;
  FABLE_DefaultParameter.CloseAngleTarget[4]=70;
  FABLE_DefaultParameter.OpenAngleTarget[0]=20;
  FABLE_DefaultParameter.OpenAngleTarget[1]=20;
  FABLE_DefaultParameter.OpenAngleTarget[2]=20;
  FABLE_DefaultParameter.OpenAngleTarget[3]=20;
  FABLE_DefaultParameter.OpenAngleTarget[4]=20;
  FABLE_DefaultParameter.isUpdated=0;
  
}

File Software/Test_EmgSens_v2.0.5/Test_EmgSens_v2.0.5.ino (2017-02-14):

// Fable_V2.0.0
//This version include the basic acquisition for the emg sensor V2.0

//LIBRARIES
#include <Servo.h>
#include "Test_EmgSens.h"
#include <EEPROM.h>
#include <EEPROMAnything.h>
#include <avr/io.h>
#include <avr/wdt.h>



//VARIABLES and data structs
int servo_pin[MAX_SERVOS]={3,5,6,9,10,11};   //servo control lines
int csens_pin[MAX_SERVOS]={A1,A2,A3,A4,A5};  //current sensor control line
int Button_Pin[MAX_BUTTONS]={4}; //Buttons control line
int simbtn =4;
boolean hand_open = true;
boolean blinkState;
boolean DiagMode=false;
String inString = "";  
String msgBuf;
boolean MacroKey=false;
int TrigEvents=0;
boolean EMG_Calib=false;

//void (*ResetFunct)(void)=0;

void setup() {
  // Initialization// 
 
  Serial.begin(serial_baude_rate);
  //Reset stato calibrazione//
  
    EMG_Calib=false;
   
   //Read parameter value in EE
   
   EEPROM_readAnything(0, FABLE_InfoParameter);
  //Scrittura in EE dei parametri di default
  //SetDefaultParameter();
  //EEPROM_writeAnything(0,FABLE_DefaultValue);
  //EEPROM_readAnything(0, FABLE_InfoParameter);
  // Inserire menu per modifica dei parametri di default//
  
  
  FABLE_EMGCH0={A0,0,0,0};
  
  
   time0=millis();
   
  // Initialize Servos//
  for (int i=0;i<MAX_SERVOS;i++){
    ioCmd[0]=0;ioCmd[1]=i;ioCmd[2]=servo_pin[i];
    Servo_Attach(ioCmd);
    ioCmd[2]=95; // Imposta il valore di velocit dei servo 
    Set_Servo_Speed(ioCmd);
    } 
 
 // Initialize Buttons//
 for (int i=0;i<MAX_BUTTONS;i++){
    pinMode(Button_Pin[i], INPUT);
    digitalWrite(Button_Pin[i],LOW);}
   // pinMode (simbtn,OUTPUT); 


  DiagMode=EnterDiag();
   while(DiagMode){
     MFL_process();
     }
//Calibrazioni  
if (EMG_Calib==false){
  EMG_calibrate_proc();
}

// digitalWrite(13,HIGH);
 
  
}

void loop() {
  // acquisition & filtering EMG

  long StartAcquisition=millis();
  while ((millis()-StartAcquisition)<MAX_TRIG_TIME){
        EMG_oversampled=oversampling(FABLE_EMGCH0.Channel,FABLE_InfoParameter.OverRatio);
        looptime=millis()-elapsedtime-StartAcquisition;
        EMG_Cmp=ComplementaryFilt(EMG_oversampled,EMG_oversampled,looptime);
        TrigEvents +=(EMG_Cmp>FABLE_EMGCH0.emg_thr)?1:0;
        elapsedtime=(millis()-StartAcquisition);
        SendGUIEMGData(ADCtoVolt(EMG_Cmp,FABLE_InfoParameter.OverRatio));
  }
  // Verifica attivazione Servo 
  MacroManager(1);
  
  
  /*Serial.print(FABLE_EMGCH0.emg_thr);
  Serial.print(';');
  Serial.print(ADCtoVolt(EMG_oversampled,FABLE_InfoParameter.OverRatio),DEC);
  Serial.print(';');
  Serial.print(hand_open);
  Serial.print(';');
  Serial.print(TrigEvents);
  Serial.print(';');
  Serial.print(StartAcquisition);
  Serial.print(';');
  Serial.println(ADCtoVolt(EMG_Cmp,FABLE_InfoParameter.OverRatio),DEC);*/
   TrigEvents=0;

  elapsedtime=(millis()-time0);
}

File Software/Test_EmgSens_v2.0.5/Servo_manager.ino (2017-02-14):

void Servo_Attach(unsigned char data[64]){

  servo_type& s = servos[data[1]];
  s.Servoindex = data[1];
  Serial.print(s.Servoindex);
  Serial.print(data[2]);
  if (s.servo == NULL){
    s.servo = new Servo();
  }
  s.servo->attach(data[2],1000,3500);
  s.step = 1;
  s.eventsEnabled = false;
}

void Servo_Sweep_Start(unsigned char data[64]){

    servo_type& s = servos[data[1]];
    s.min = data[2];
    s.max = data[3];
    s.step = data[4];
    s.isMoving = true;
    s.isSweeping = true;
}

void Servo_Sweep_Stop(unsigned char data[64]){
      servo_type& s = servos[data[1]];
      s.isMoving = false;
      s.isSweeping = false;
}

void Servo_write(unsigned char data[64]){
  servo_type& s = servos[data[1]];
  if (s.speed == 100 && s.servo != 0)// move at regular/full 100% speed
  {
     s.targetPos = data[2];
	   s.currentPos = data[2];
	   s.isMoving = false;
     s.servo->write(data[2]);
     if (s.eventsEnabled) sendServoEvent(s, SERVO_EVENT_STOPPED);
  } else if (s.speed < 100 && s.speed > 0) {
	    s.targetPos = data[2];
	    s.isMoving = true;
  }
//Serial.print("write");
//Serial.print(s.targetPos);
//Serial.println(s.speed);
}


void Servo_Write_Microseconds(unsigned char data[64]){

  servo_type& s = servos[data[1]];
  if (s.servo != 0) {
	// 1500 midpoint
	s.servo->writeMicroseconds(data[2]);
  }

}

void Set_Servo_Speed(unsigned char data[64]){
// setting the speed of a servo
  servo_type& servo = servos[data[1]];
  servo.speed = data[2];
}

void Servo_Events_Enable(unsigned char data[64]){
//enable debug write on serial
servo_type& s=servos[data[1]];
s.eventsEnabled=data[2];
}


void Servo_Detach(unsigned char data[64]){
  servo_type& s = servos[data[1]];
  if (s.servo != 0){
	s.servo->detach();
  }
}


void ServoTestManager(int loopCount){
  
  for (int i = 0; i < MAX_SERVOS; ++i)
	{
		
    servo_type& s = servos[i];
                
	    if (s.isMoving && s.servo != 0){
              //s.eventsEnabled=true;
            if (s.currentPos != s.targetPos)
	    {
				    // caclulate the appropriate modulus to drive
				    // the servo to the next position
				    // TODO - check for speed > 0 && speed < 100 - send ERROR back?
				    int speedModulus = (100 - s.speed) * 10;
				
            if (loopCount % speedModulus == 0)
		{  //if (ServoOvercurrent(i)){
                     //s.targetPos-= FABLE_InfoParameter.OvercurrentAngle;
                    //}
			int increment = s.step * ((s.currentPos < s.targetPos)?1:-1);
			// move the servo an increment
			s.currentPos = s.currentPos + increment;
			s.servo->write(s.currentPos);
			if (s.eventsEnabled) sendServoEvent(s, SERVO_EVENT_POSITION_UPDATE);
		 }
		} else {
			if (s.isSweeping) {
				if (s.targetPos == s.min){
					s.targetPos = s.max;
				} else {
					s.targetPos = s.min;
					}
				} else {
					if (s.eventsEnabled) sendServoEvent(s, SERVO_EVENT_STOPPED);
					s.isMoving = false;
				}
			}
		}s.eventsEnabled=false;
	}

}

void ServoMovement(int servoindex){
  
    
    servo_type& s = servos[servoindex];
                
    while (s.isMoving && s.servo != 0){
    loopCount++;
            s.eventsEnabled=false;
            if (s.currentPos != s.targetPos)
           {
            // caclulate the appropriate modulus to drive
            // the servo to the next position
            // TODO - check for speed > 0 && speed < 100 - send ERROR back?
            int speedModulus = (100 - s.speed) * 5;     
          if (loopCount % speedModulus == 0)
         {
            if (ServoOvercurrent(servoindex)){
                //  s.targetPos-= FABLE_InfoParameter.OvercurrentAngle;
            }
            int increment = s.step * ((s.currentPos < s.targetPos)?1:-1);
            // move the servo an increment
            s.currentPos = s.currentPos + increment;
            s.servo->write(s.currentPos);
            if (s.eventsEnabled) sendServoEvent(s, SERVO_EVENT_POSITION_UPDATE);
         }
        }
         else {
          if (s.eventsEnabled) sendServoEvent(s, SERVO_EVENT_STOPPED);
          s.isMoving = false;
        }
      }
    s.eventsEnabled=false;
} 




void OpenCloseActivation(){
    
    if (TrigEvents>MAX_TRIG_EVENTS){   
    if (hand_open){
    //close Hand
    Serial.println("CLOSE HAND");
    for (int i = 0; i < MAX_SERVOS; ++i){
      servo_type& s = servos[i];
      ioCmd[0]=0;ioCmd[1]=i;ioCmd[2]=FABLE_InfoParameter.CloseAngleTarget[i];
     // Serial.println(FABLE_InfoParameter.CloseAngleTarget[i]);
      Servo_write(ioCmd);
      ServoMovement(i);
    }
    hand_open=false;
    }else{
    Serial.println("OPEN HAND");
    for (int i = MAX_SERVOS; i > 0; --i){
      servo_type& s = servos[i];
      ioCmd[0]=0;ioCmd[1]=i;ioCmd[2]=FABLE_InfoParameter.OpenAngleTarget[i];
      //Serial.println(FABLE_InfoParameter.OpenAngleTarget[i]);
      Servo_write(ioCmd);
      ServoMovement(i);
  }
  hand_open=true;}
 }

}

void MacroKeyActivation(){
  //Close
  
   if (TrigEvents>MAX_TRIG_EVENTS){   
    if (hand_open){
    //close Pollice
    Serial.println("Close Poll");
      servo_type& s = servos[MAX_SERVOS-1];
      ioCmd[0]=0;ioCmd[1]=MAX_SERVOS-1;ioCmd[2]=FABLE_InfoParameter.CloseAngleTarget[MAX_SERVOS-1];
     // Serial.println(FABLE_InfoParameter.CloseAngleTarget[i]);
      Servo_write(ioCmd);
      ServoMovement(MAX_SERVOS-1);
   hand_open=false;
    }
    
    else{
    Serial.println("Open Poll");
      servo_type& s = servos[MAX_SERVOS-1];
      ioCmd[0]=0;ioCmd[1]=MAX_SERVOS-1;ioCmd[2]=FABLE_InfoParameter.OpenAngleTarget[MAX_SERVOS-1];
      //Serial.println(FABLE_InfoParameter.OpenAngleTarget[i]);
      Servo_write(ioCmd);
      ServoMovement(MAX_SERVOS-1);
      hand_open=true;
    }
  }
 
 
 

}


void sendServoEvent(servo_type& s, int eventType){
  	// check type of event - STOP vs CURRENT POS

	Serial.print(MAGIC_NUMBER);
	Serial.print(5); // size = 1 FN + 1 INDEX + 1 eventType + 1 curPos
	Serial.print(SERVO_EVENT);
	Serial.print(s.Servoindex); // send my index
	// write the long value out
	Serial.print(eventType);
	Serial.print(s.currentPos);
        Serial.println(s.targetPos);
        
    
}
// Servo Overcurrent manager //
boolean ServoOvercurrent(int servoindex){
  
 csens_val=analogRead(csens_pin[servoindex]);
  if (csens_val>FABLE_InfoParameter.csens_thr)
     return true;
 else
     return false;

}

//MACRO MANAGER//
void MacroManager(int caller){
int BtnReading;

 
  
 for (int i = 0; i < MAX_BUTTONS; ++i){
    switch(caller){
     case 1:{ 
     BtnReading = digitalRead(Button_Pin[i]);
     break;}
     case 0:{
       if (i==SimButton[i].BtnIndex)
           BtnReading=SimButton[i].buttonState;
       break;}
    }
  // check to see if you just pressed the button
  // (i.e. the input went from LOW to HIGH),  and you've waited
  // long enough since the last press to ignore any noise:

  // If the switch changed, due to noise or pressing:
//  if (BtnReading != FableButton[i].lastButtonState) {
//    // reset the debouncing timer
//      FableButton[i].lastDebounceTime = millis();
//   }
//   if ((millis() - FableButton[i].lastDebounceTime) > FableButton[i].debounceDelay) {
//////    // whatever the reading is at, it's been there for longer
//////    // than the debounce delay, so take it as the actual current state:
//////    
//    
//////    // if the button state has changed:
      if (BtnReading != FableButton[i].buttonState) {
      FableButton[i].buttonState = BtnReading;
      }
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
